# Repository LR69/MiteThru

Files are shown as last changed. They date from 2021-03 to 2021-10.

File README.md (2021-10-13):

# MiteThru

MiteThru is a raspberry based system used to count red mites going to/from a hen. 

It can count [one mite](https://www.youtube.com/watch?v=HM9iWV7Sr2Q),

VIDEO1 (https://www.youtube.com/watch?v=HM9iWV7Sr2Q)

Or, [many mites](https://www.youtube.com/watch?v=uRkvY6X4qfg) at the same time 

VIDEO2 (https://www.youtube.com/watch?v=uRkvY6X4qfg)

This MiteThru system uses :

- a raspberry pi 3 model B programmed using [python3](https://docs.python.org/3/) language,
- a native pi camera V2 Night Vision NoIR with a resolution of 8 mega-pixel,
- infrared Leds used to illuminate the mites,
- an electronic board with some push buttons, colored led and power devices to control the system,
- some Lego parts for a quick assembly.

The complete list of required components is available in the [Bill Of Materials](https://github.com/LR69/MiteThru/blob/master/Bill_Of_Material.ods)

# How the miteThru works:

A miteThru is a device that counts mites ascending and descending from a perch, where a hen is staying. It is able to classify them according to their size. The miteThru uses an infrared camera, to visualize the mites.

A circular boundary is placed around the roost. Mites passing inside this circle are considered "IN", mites outside are considered "OUT". To avoid indecision due to mites standing on the line, or moving around it, a counting or hysteresis zone is defined. The mite that is "OUT" has to cross the inner disc of the counting zone to go to "IN". The mite that is "IN" must cross the outer disc of the counting zone to go to "OUT".

## Counting principle

The miteThru places on the registered view :

- A monitoring area (in light gray) 
- A referencing zone (in dark gray)
- A counting area (in green)
- A border  (in red)

<table>
	<tr>
		<td width="300">  </td>
		<td>Step 1 : If a mite enters the tracking area, it is "seen" by the software, but has no visible identifier.</td>
	</tr>
	<tr>
		<td> </td>
		<td> Step 2 : If the mite fits into the referencing area, it is assigned an ID and its area is materialized by a colored disk that is superimposed on the image. The color of the disk indicates how the mite is classified according to its size. 

The size of the mite is updated with each image taken by the miteThru. </td>
	</tr>
	<tr>
		<td> </td>
		<td>Step 3: If the mite enters the counting area from the outside and leaves from the inside, the "IN" counter associated with its mite category is incremented.
If the mite enters the counting area from the inside and leaves from the outside, the "OUT" counter associated with its mite category is incremented.
		</td>
	</tr>
	<tr>
		<td></td>
		<td> Step 4: If the mite leaves the referencing area, it loses its identifier.
The identifiers are incremented as the mites enter the referencing area. 
The identifier can range from 0 to 99999. If a 100000th mite is tracked, its identifier returns to zero.</td>
	</tr>
	
</table>

# Commissioning

## Connecting the miteThru

The MiteThru uses a board equipped with LEDs and Push Buttons to start, stop and reset acquisitions locally. The board also power the IR LEDs illuminating the mites. All the schematics and Typon of the board can be found in the "[electronic board](https://github.com/LR69/MiteThru/tree/master/electronic%20board)" folder of this repository.

Connect the +5V power supply wires of the raspberry motherboard (brown and white wire), the +12V power supply of the circuit (wires coming from the AC/DC adapter), and the 2 wires of the infrared LEDs to the terminal block of the electronic board, as shown below. Make sure that the AC/DC adapter is not connected to the 230VAC wall socket during the connection operations.

Wiring the MiteThru

## Operating the MiteThru

3 push buttons are present on the [electronic board](https://github.com/LR69/MiteThru/tree/master/electronic%20board) :

MT_Buttons

## Start Acquisition 
Press the **<a name="start_BP">Start/Stop button</a>** for at least 3 seconds 
	→ The green LED flashes rapidly (several times per second), which means that the acquisition program is running.

<u>Note</u>: if the power supply is interrupted or if the power supply is disconnected while the program was running, it will restart automatically when the power is restored.

## Record Images

Press and hold the **<a name="record_BP"> Record button</a>**	
									→ Image recording starts
									→ Yellow LED lights up

Release of the **<a name="record_BP2"> Record button</a>**					
									→ Yellow LED goes out
									→ Image recording stops

## Stop Acquisition 

Press briefly the **<a name="start_BP2">Start/Stop button</a>** 
	→ The green LED goes out, which means that the acquisition program has stopped.

<u>Note</u>: After the program has been stopped, it can be restarted using the Start/Stop button, without losing the previous data. The new data are then added after the others.

## Reset Acquisition 

The miteThru must be turned off (green LED off) in order to begin the erasure procedure.

Press and hold the **<a name="reset_BP">Reset button</a>** 
	→ The green LED lights up blinks quickly.
	After about 5 seconds, the green LED lights up steadly 
	Release the **<a name="reset_BP">Reset button</a>** within 2 seconds
		→  The green LED lights up continuously for 2 seconds, then goes out. 

The miteThru is then cleared.

<u>Note</u>: After a RESET, the html pages of the miteThru do not automatically update, you must restart the acquisition program so that the "Data" and "Live" tabs update. In the same way, the "Images" tab will only be updated if new images are acquired.

# Monitoring and Data Recovery

The MiteThru embeds an Apache 2 server which provides a Web Interface, written in `html` and `php`. To access the interface, connect the MiteThru using Wifi or with an Ethernet cable. Then open a Browser and type the IP address of the MiteThru :

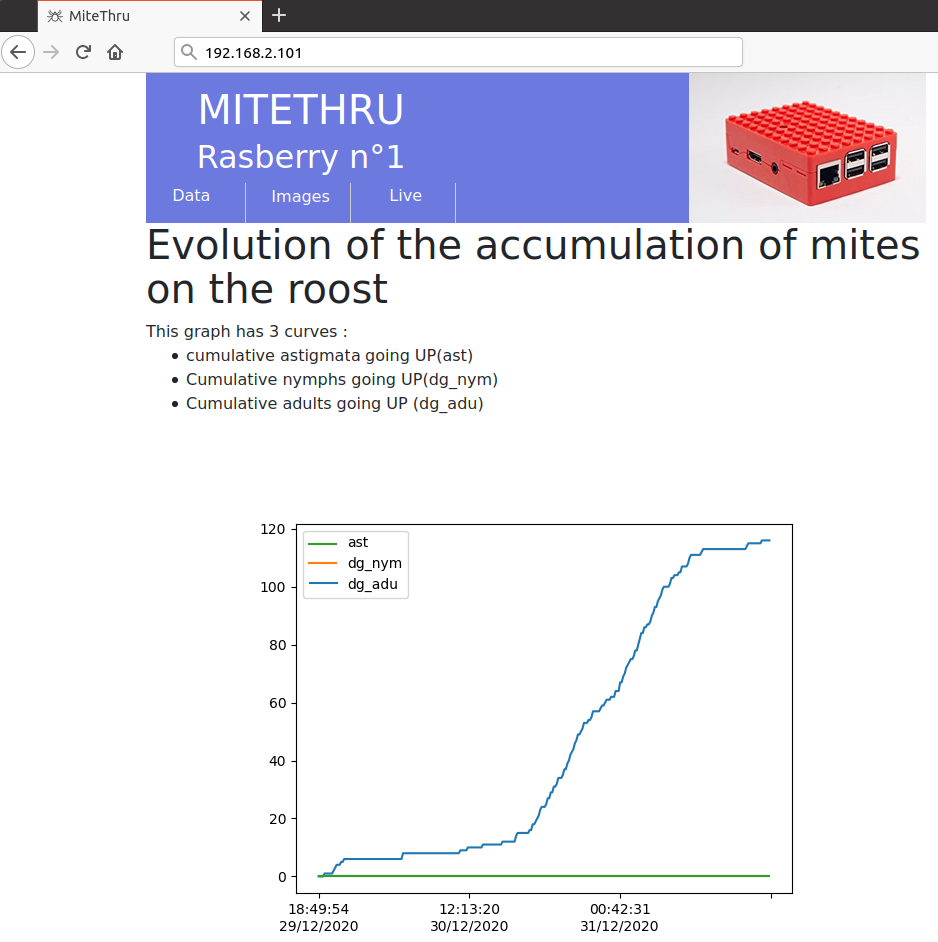
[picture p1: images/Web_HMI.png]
MT_HMI


## Tab "Data"

The web interface shows the temporal evolution of the Mites counted since the beginning of the acquisition. 3 diagrams can be seen :

- One showing the cumulative Mites going on the perch.
- An other showing  the cumulative Mites going down from the perch.
- A last one showing the instantaneous rate of climb or descent 

At the bottom of the tab, data of the experiment can be downloaded at `.csv` format by clicking on 
<div style="text-align:center">
	Button Download 
</div>

## Tab "images"

When the Push  [Record button](#record_BP)	 has been used to store images, this tab is used to check and download the images. Images are displayed as a link to the raw and processed images (at the bottom of the page). All the images of a record are available at download as a `.zip` file containing images at `.jpg` format. 

- Download the zip of the images by clicking on the links, then unzip the images and check that they are viewable. 
- If needed, jpeg images can be added (using [ffmpeg](https://www.ffmpeg.org/) for instance), to form a video like these presented at the top of this Readme. 

This tab can also be used to trigger automatically video acquisitions, on a certain level of mites being tracked at the same time, or on a periodic basis.

## Tab "Live"

On this page, two images are continuously updated by the program. 

1. The first image is the raw image take by the camera,
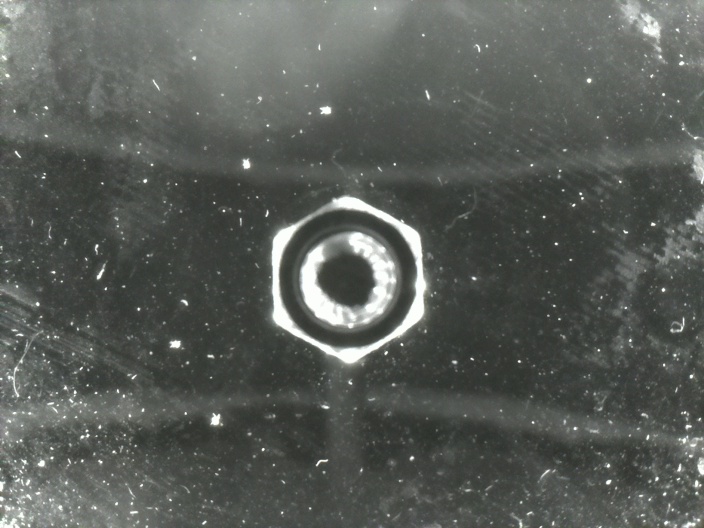
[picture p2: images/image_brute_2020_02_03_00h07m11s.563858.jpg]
image_brute
    
2. On the second image, elements related to image processing have been added.
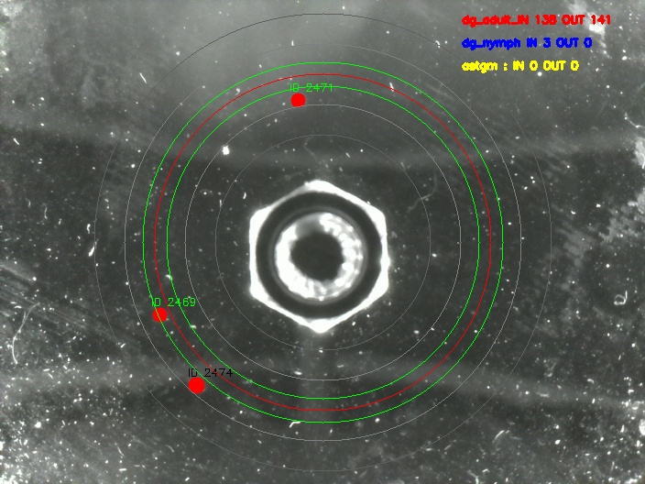
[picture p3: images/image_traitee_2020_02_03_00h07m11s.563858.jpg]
imag_traitée


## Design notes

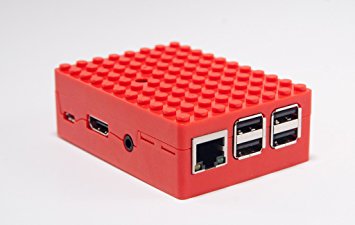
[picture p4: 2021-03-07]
raspberry/html/images/RPi_Lego.jpg

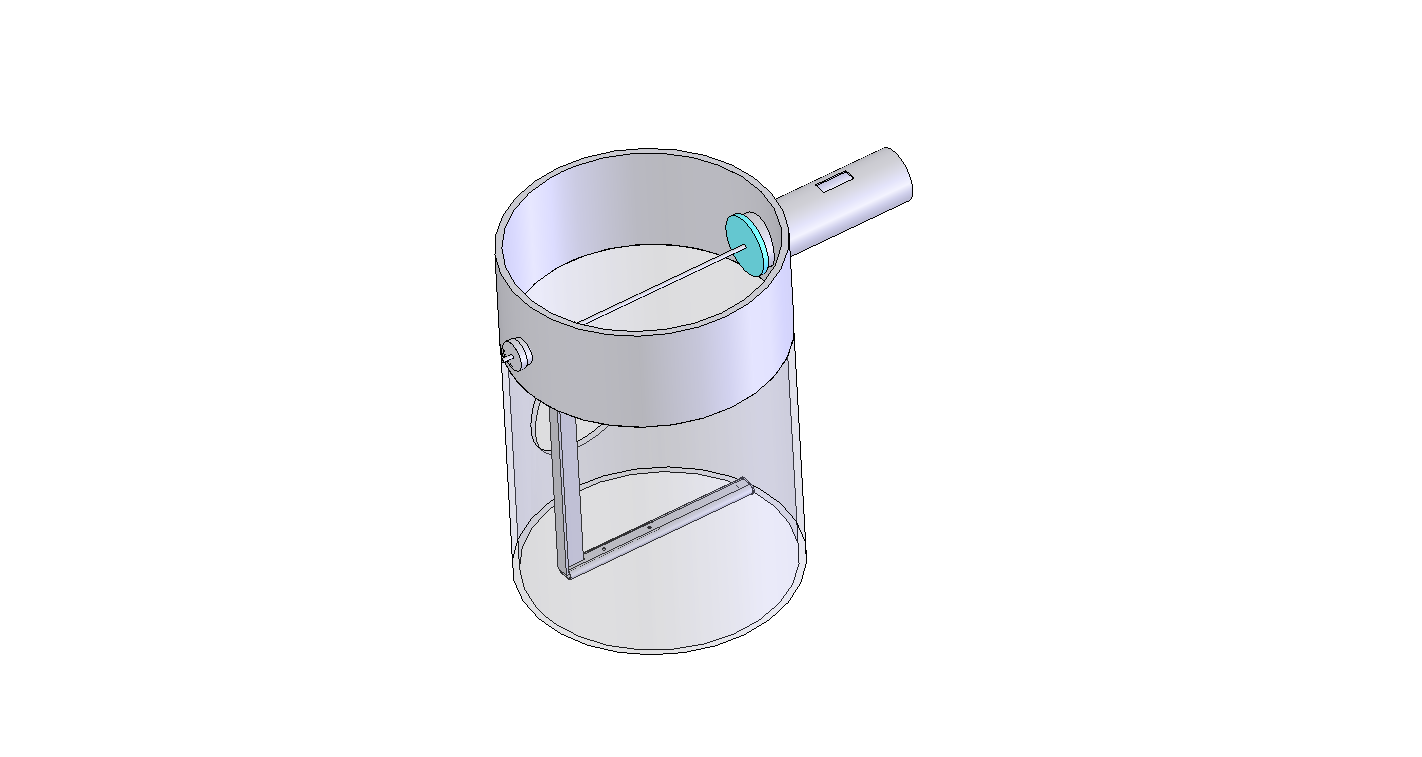
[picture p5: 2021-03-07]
technical drawings/mite_track_v1e.tif

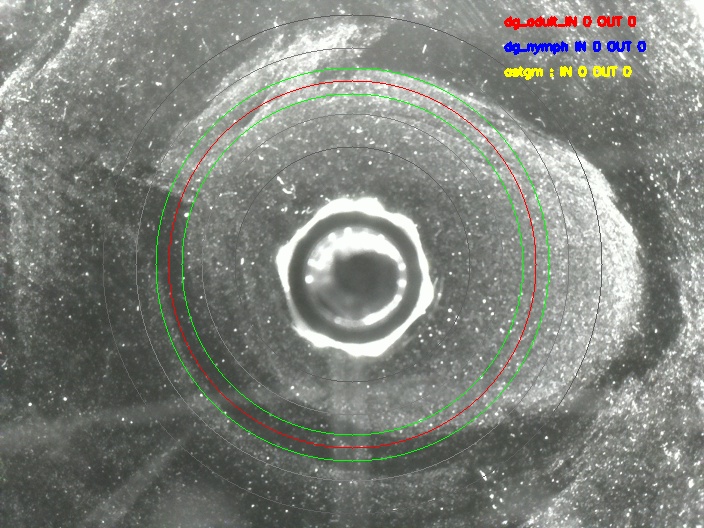
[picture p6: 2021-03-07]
raspberry/html/images_bugcount/live/image_traitee.jpg

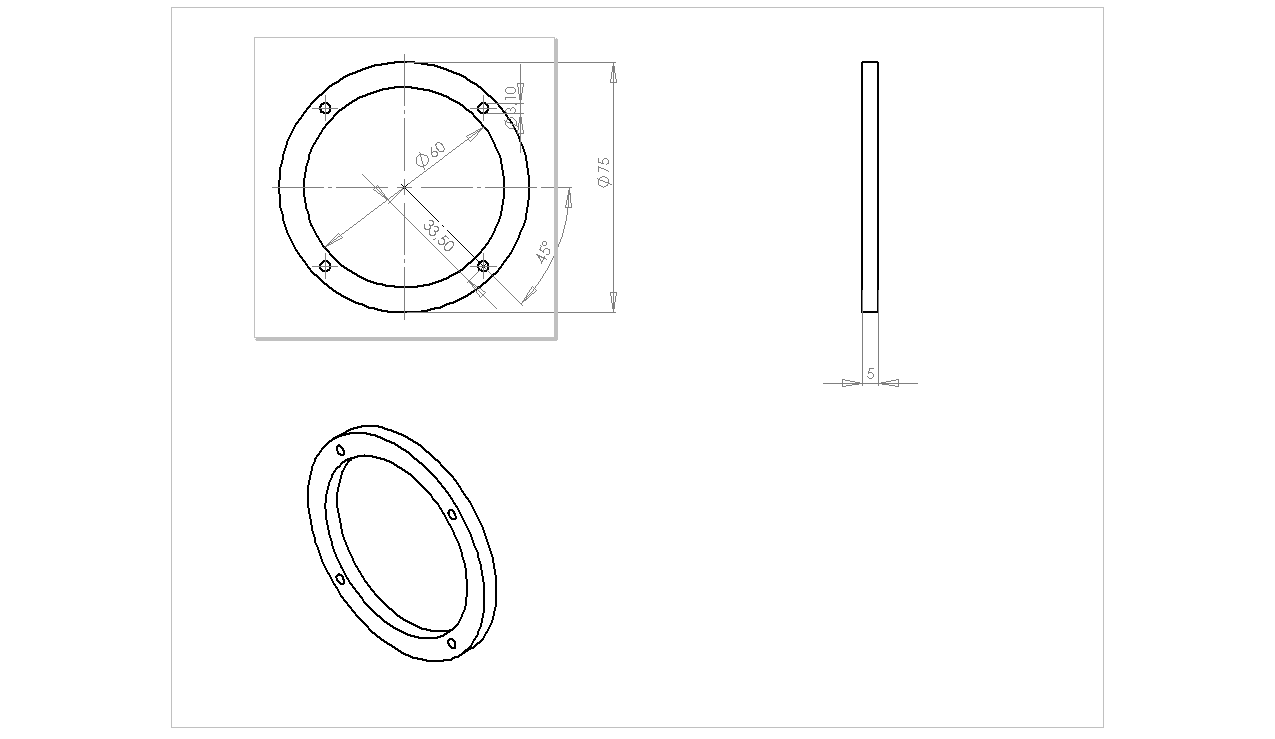
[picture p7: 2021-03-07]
technical drawings/washer.tif

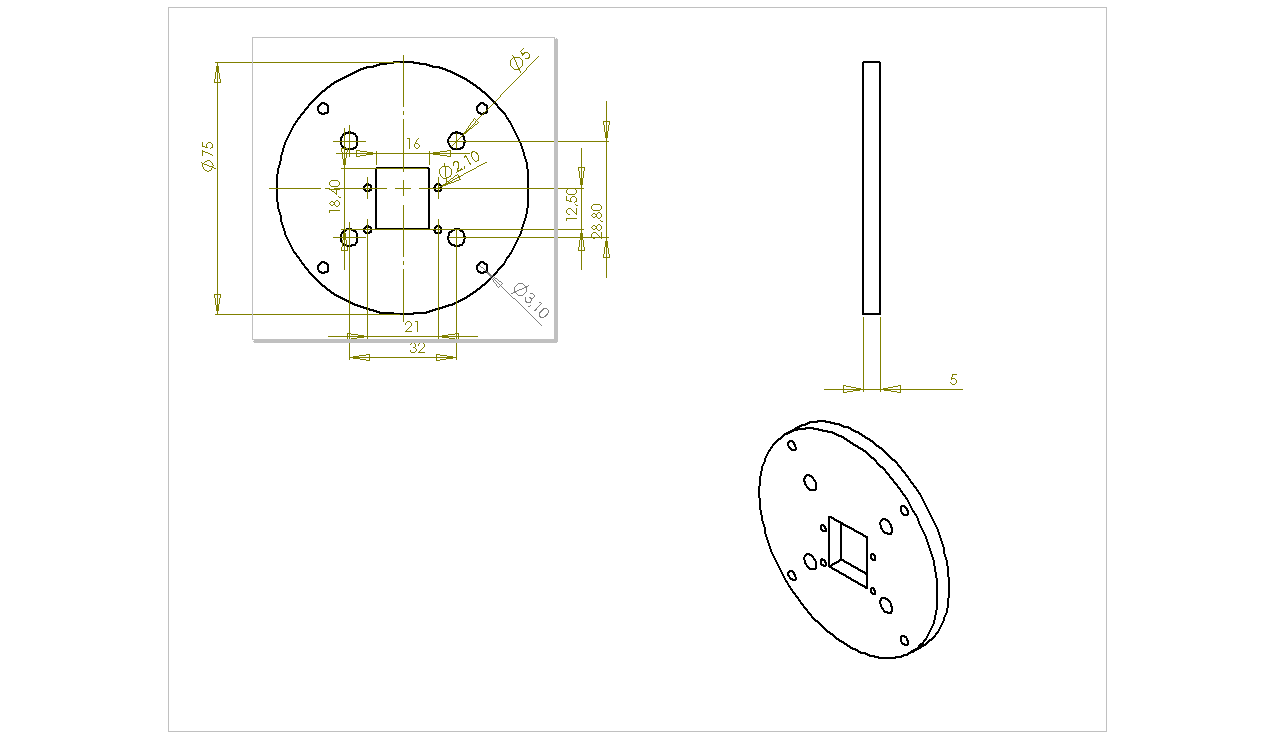
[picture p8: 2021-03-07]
technical drawings/camera_support.tif

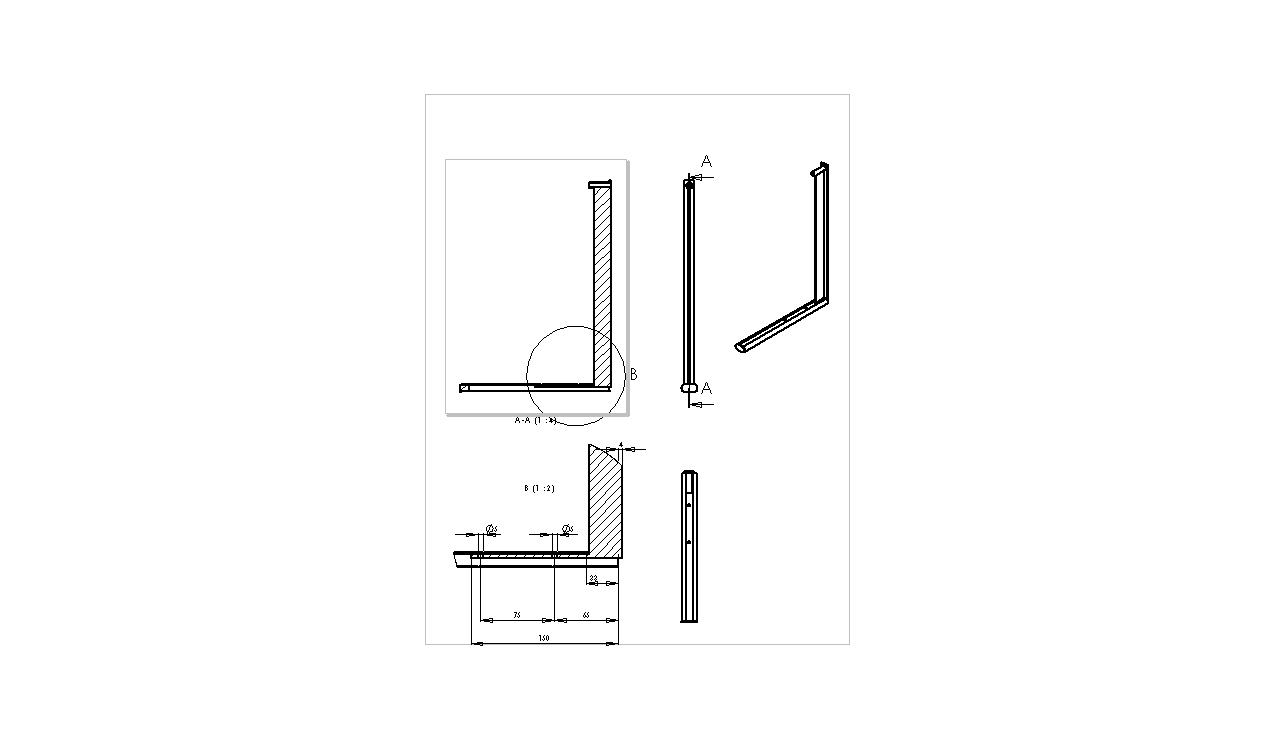
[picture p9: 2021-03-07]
technical drawings/balancoire_mbv1e.tif

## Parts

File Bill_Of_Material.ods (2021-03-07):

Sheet: MiteThru
Part | Description | Manufacturer | Reference | Quantity
Mechanics | Disc plexi diam :90mm thick : 5mm | Home made |  | 1
Mechanics | DiscPVC D75 mm for camera | Home made |  | 1
Mechanics | DiscPVC D75 mm for fan | Home made |  | 1
Mechanics | srew diam 4 mmround head L=25mm |  |  | 4
Mechanics | bolts diam 4 mm |  |  | 4
Mechanics | Screw diam 2 mm round head L=10mm |  |  | 4
Mechanics | Bolt diam 2 mm |  |  | 4
Mechanics | Tube PVC 80mm L=220mm |  |  | 1
Mechanics | threaded rod 3mm L= 120mm |  |  | 1
Mechanics | bolt 3mm |  |  | 2
Mechanics | lock washer 3 mm |  |  | 2
Mechanics | washer 3 mm |  |  | 2
Mechanics | Round 1 x 1 Straight Side | Lego | 4073 | 4
Mechanics | Brick 8x1 | Lego | 3008 | 1
Mechanics | Brick 6x1 |  | 3009 | 1
Mechanics | Brick 14x1 |  | 32018 | 2
Mechanics | Brick 8x1 w holes | Lego | 3702 | 3
Mechanics | Brick 6x1 w holes | Lego | 3894 | 1
Mechanics | Brick 1x1 |  | 3005 | 6
Mechanics | plate 6x2 |  | 3795 | 2
Mechanics | plate 4x1 |  | 3710 | 4
Mechanics | plate 8x1 |  | 3460 | 1
Mechanics | plate 8x2 |  | 3034 | 1
Mechanics | plate 14x2 |  | 91988 | 1
Computing | CBPIBLOX-YEL. - Pi Box, Raspberry Pi Model B, B+, 2 and 3 ABS | Multicomp |  | 1
Computing | Axial Fan, 40 x 40 x 10mm 11.4m3/h, 1,2W 12VDC
Computing | Raspberry 3 model B |  |  | 1
Computing | SD Card 16 GB UHS-I (U3) / Class 10 (C10) microSDHC/TF Flash Memory Card | Alertseal |  | 1
Computing | Raspberry Pi Module Caméra Raspberry Pi PiNoir Camera V2 |  |  | 1
Electronics | Strip 15 leds IR – L = 28cm IR 940nm | SOLAROX | IR1-60-940 | 1
Electronics | MOSFET, Canal-N, 47 A 55 V TO-220AB |  |  | 1
Electronics | AC/DC Adapter 12V c.c., 0 → 1A, 90 → 264V c.a., 12W |  |  | 1
Electronics | DC/DC Converter Vin 7 → 28V c.c., Vout 5V c.c., 500mA, 2.5W | RECOM |  | 1
Electronics | Pi RTC (DS1307) – only for server |  |  | 1
Electronics | polyester capacitor PET EPCOS, 1μF, ±10%, 40 V ac, 63 V dc, Through-hole, 5mm pitch, B32529 |  |  | 1
Electronics | D2,LED_JLED_THT:LED_D3.0mm |  |  | 1
Electronics | D1,LED_RLED_THT:LED_D3.0mm |  |  | 1
Electronics | D3,LED_VLED_THT:LED_D3.0mm |  |  | 1
Electronics | 2-contact PCB socket, through hole mounting, 5.08mm pitch, vertical |  |  | 2
Electronics | metallic film resistor 100Ω, 0,25W, |  |  | 1
Electronics | Resistor 270Ω, 0,25W, ±5% |  |  | 2
Electronics | resistor 680Ω, 0,25W, ±5% |  |  | 1
Electronics | resistor 10kΩ, 0,25W, ±5% |  |  | 1
Electronics | Tactile switch, 1NO - NO, 50mA/24Vdc, Black 5mm Push Button B3F-1020 | OMRON |  | 3

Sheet: Vocab
Statut
Commandé
Livraison en Cours
Reçu
Problème

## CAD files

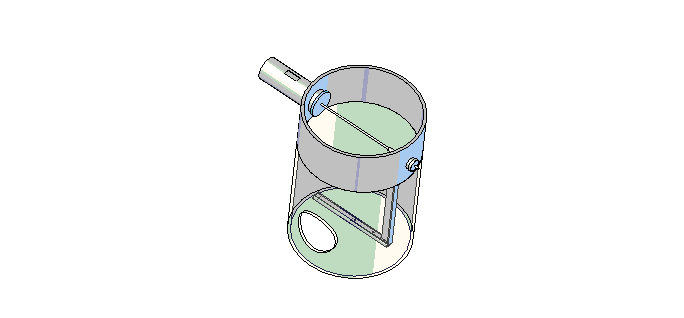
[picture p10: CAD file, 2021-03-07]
technical drawings/mite_track_v1e.SLDASM
Buse
tuyau
disque_plexi
tige filetée
TuyauDN40
bouchonDN40
Mesocosme
perchoir
montant
bouchon

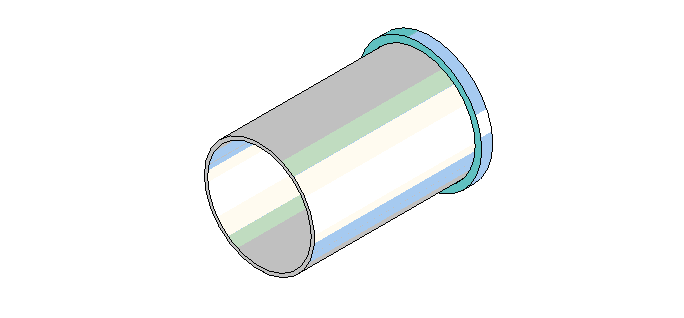
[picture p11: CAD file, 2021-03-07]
technical drawings/tuyau_disque_plexi.SLDASM
tuyau
disque_plexi

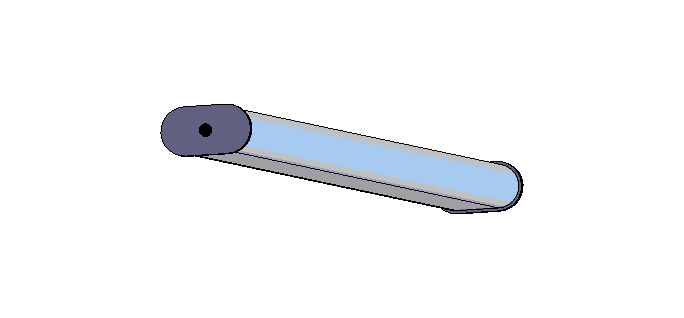
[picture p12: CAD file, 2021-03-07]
technical drawings/tige_bouchons.SLDASM
perchoir
bouchon x 2

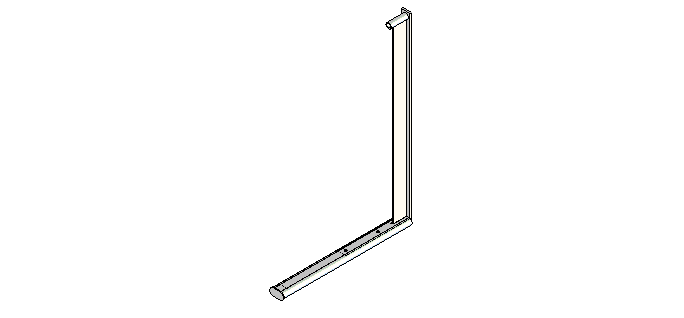
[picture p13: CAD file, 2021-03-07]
technical drawings/balancoire_mb.SLDASM
perchoir
montant
bouchon

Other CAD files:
technical drawings/Buse.SLDPRT
technical drawings/perchoir.SLDPRT
technical drawings/montant.SLDPRT
technical drawings/tige filetВe.SLDPRT
technical drawings/Mesocosme.SLDPRT
technical drawings/vis.SLDPRT
technical drawings/disque_plexi.SLDPRT
technical drawings/camera_support.SLDPRT
technical drawings/tuyau.SLDPRT
technical drawings/bouchonDN40.SLDPRT
technical drawings/TuyauDN40.SLDPRT
technical drawings/bouchon.SLDPRT
technical drawings/fan_support.SLDPRT
technical drawings/washer.SLDPRT
technical drawings/balancoire_mb.SLDDRW
technical drawings/camera_support.SLDDRW
technical drawings/fan_support.SLDDRW
technical drawings/montant.SLDDRW
technical drawings/tuyau.SLDDRW
technical drawings/washer.SLDDRW

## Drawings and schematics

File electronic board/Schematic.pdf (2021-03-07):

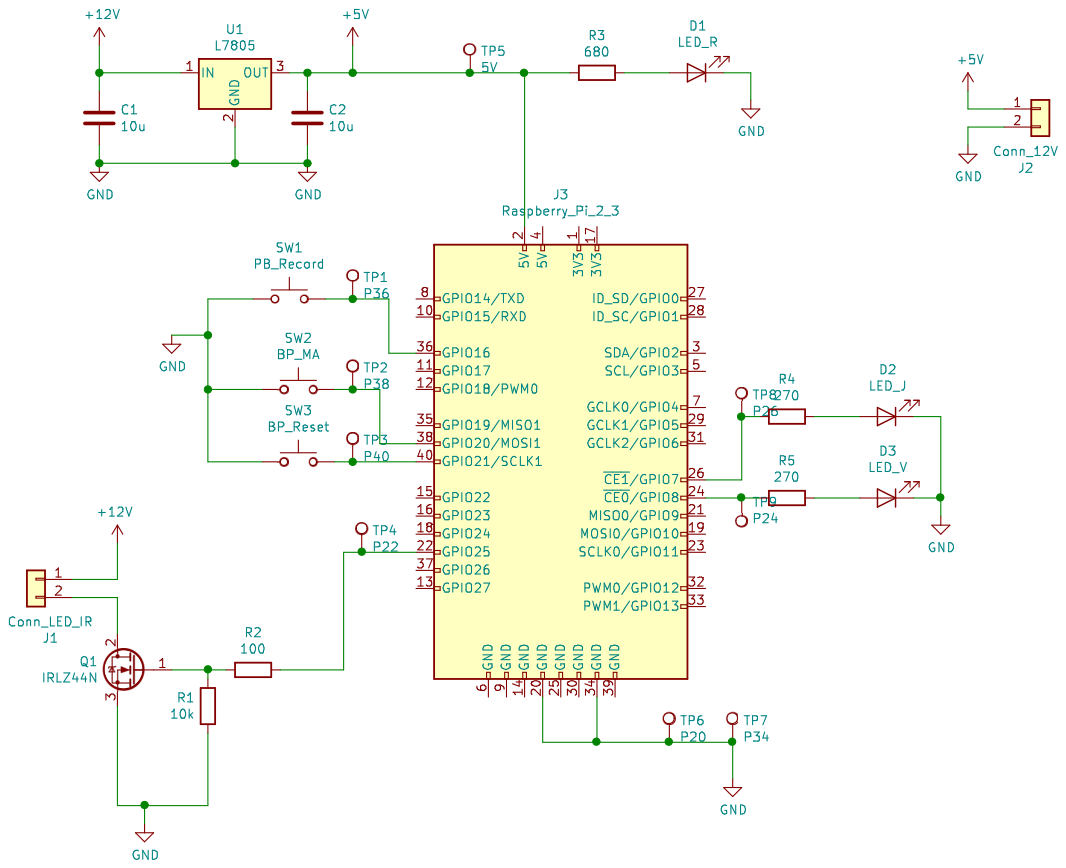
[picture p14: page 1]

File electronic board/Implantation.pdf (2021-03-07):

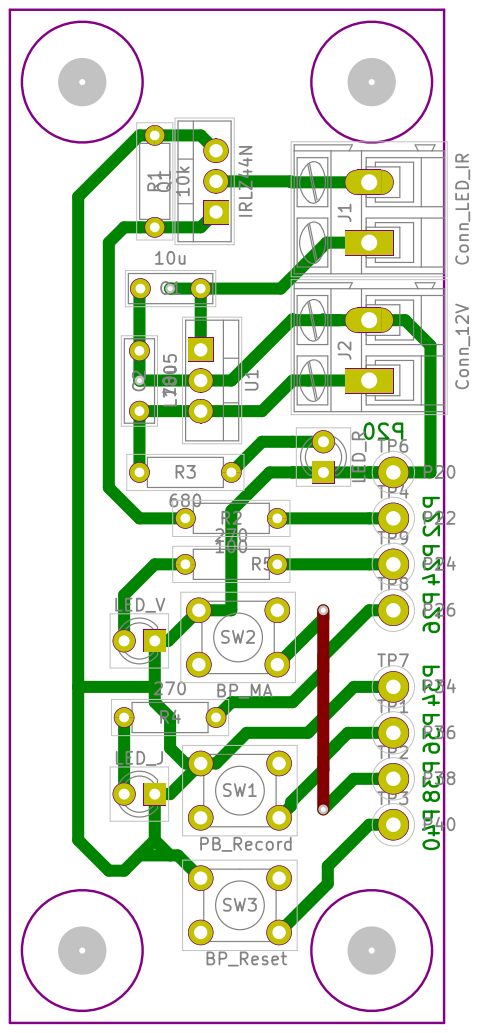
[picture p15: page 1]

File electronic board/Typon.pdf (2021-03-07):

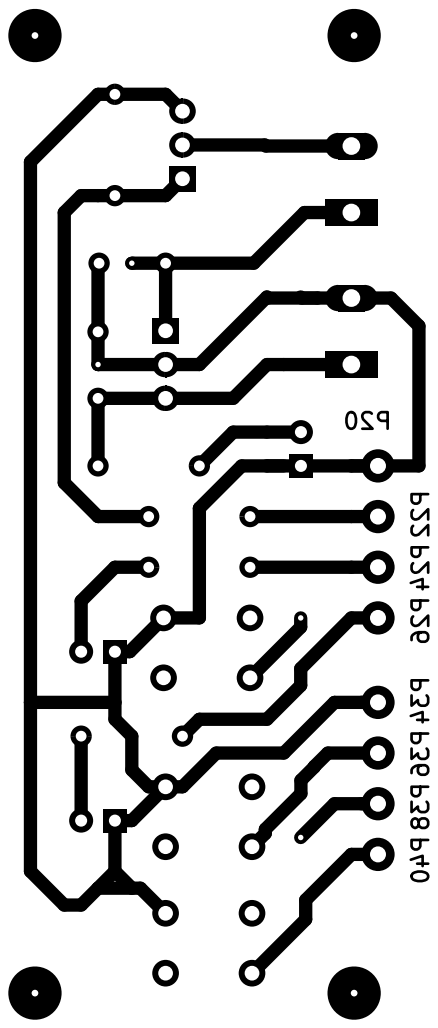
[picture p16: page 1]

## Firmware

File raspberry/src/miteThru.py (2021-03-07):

from picamera.array import PiRGBArray
from picamera import PiCamera
import numpy as np
import math
from random import randint
import cv2
import RPi.GPIO as GPIO
import time
import os
import shutil
import datetime
import sys
import bugcount_utils
import img_count_utils as imcount
from mitestracker import MitesTracker
import copy
import multiprocessing as mp #MP
import signal #MP

"""
# MiteThru version 12 du 16 juillet 2020
 """

os.nice(-5) # le programme principal est agressif

#initialisation de l'interface images
shutil.copyfile("/var/www/html/pre_index_images_ini.html", "/var/www/html/pre_index_images.html")

#Vérification de la conformité de la commande passée :
msg_gal = "ERREUR : rappel de la commande miteThru : python3 miteThruVi.py -Fe f -mode mode [s] [d] [i]"
if len(sys.argv) < 5:
	print(msg_gal)
	print("Le nombre d'argument doit être >= 3")
	sys.exit(1)

mode = sys.argv[4]
option = ""
if mode == "debug" or mode == "normal":
	if len(sys.argv) != 6:
		print(msg_gal)
		print("mode \"{}\", il faut un seul argument après le mode".format(mode))
		sys.exit(1)
	try:
		s=int(sys.argv[5])
	except ValueError:
		print(msg_gal)
		print("L'argument après le mode doit être un nombre entier")
		sys.exit(1)
elif mode == "calib_en_ligne":
	option = "calib_en_ligne"
	mode = "video"
	p0_flag = False
elif mode == "video" :
	if len(sys.argv) != 8:
		print(msg_gal)
		print("mode \"{}\", il faut 3 arguments après le mode".format(mode))
		sys.exit(1)
	try:
		s=int(sys.argv[5])
		s=int(sys.argv[6])
		s=int(sys.argv[7]) 
	except ValueError:
		print(msg_gal)
		print("L'argument après le mode doit être un nombre entier")
		sys.exit(1)
else:
	if mode != "calib":
		print(msg_gal)
		print("Le mode \"{}\" n'est pas reconnu".format(mode))
		sys.exit(1)

# gestion des modes 
seuil_video = 9999
duree_video = 1
intervalle_min_video = 99999
debug = 0
if (mode == "video"):
	seuil_video = int(sys.argv[5]) # nombre d'acariens suivis déclenchant une acquisition video
	duree_video = int(sys.argv[6]) # duree de l'acquisition vidéo (en secondes)
	intervalle_min_video = int(sys.argv[7]) # intervalle minimum entre deux acquisitions videos (en secondes)
	texte="<h1>Aquisition automatique de vidéos</h1>\n <ul>\n"
	if option != "":
		texte+="<li>option : {}</li>\n".format(option)
	texte+="<li>nombre d'acariens suivis déclenchant une acquisition video : {}</li>\n".format(seuil_video)
	texte+="<li>duree de l'acquisition vidéo (en secondes) : {}</li>\n".format(duree_video)
	texte+="<li>intervalle minimum entre deux acquisitions videos (en secondes):{}</li>\n</ul>\n".format(intervalle_min_video)

elif (mode == "normal"):
	texte="<h1>Aquisition automatique de vidéos</h1>\n \n"
	if int(sys.argv[5]) == 0:
		texte+="<p> L'acquisition automatique a été désactivée par l'utilisateur.</p>"
	else:
		texte+="<p> L'acquisition automatique a été désactivée car la taille totale des images sur la carte SD dépasse 1GB. Pensez à faire un Reset.</p>"
elif (mode == "calib"):
	texte="<h1>Aquisition automatique de vidéos</h1>\n \n"
	texte+="<p> Le miteThru est en mode CALIBRATION. L'acquisition est forcée à une image par seconde.</p>"
	texte+="<p> Aucun enregistrement vidéo n'est effecué.</p>"
	texte+="<p> Les données d'aires sont mémorisée dans un fichier \"data.csv\".</p>"
elif (mode == "debug"):
	debug = int(sys.argv[5]) # niveau de nervosité du debug 
	texte="<h1>Aquisition automatique de vidéos</h1>\n \n"
	texte+="<p> Le miteThru est en mode Debug. avec un niveau de verbosité de {}</p>".format(debug)
# Gestion de la fréquence d'échantillonnage
try:
	Fe = int(sys.argv[2]) # fréquence d'échantillonage
except ValueError:
	print(msg_gal)
	print("La frequence d'échantillonnage doit être un nombre entier")
	sys.exit(1)

with open('/var/www/html/pre_index_images.html','a') as preamb:
	if Fe == 0 :
		texte+="<p> La fréquence d'échantillonnage n'est pas limitée</p>"
	else:
		texte+="<p> La fréquence d'échantillonnage maximale est fixée à {} images par secondes</p>".format(Fe)
	texte+="<p></p>"
	texte+="<h1>Images mémorisées </h1>\n"
	texte+="\t<div align=center>\n"
	texte+="\t\t<table>\n"
	preamb.write(texte)
	print(texte) #pour le log
if Fe == 0:
	Fe = 99999 # pas de limitation
temps_cycle = 1000/Fe #temps de cycle minimum


# pour le mode debug 8 = forçage de reset 
bypass_reset = False
if debug == 8:
	bypass_reset = True
	with open("stop_normal",'w') as mon_fichier:
		mon_fichier.write("forçage de reset en mode debug")
		

# gestion du redémarrage après coupure de courant
if os.path.exists("stop_normal"):
	bypass = False
else:
	bypass = True

# pour le mode debug 9 = forçage de lancement
if debug == 9:
	bypass = True

# initialisation des pins du rpi
GPIO.setmode(GPIO.BCM)
GPIO.setwarnings(False)

# entrées
BPrecord = 16 # Bouton enregistrement : pin 36
GPIO.setup(BPrecord, GPIO.IN,pull_up_down=GPIO.PUD_UP) 
BPma = 20  # bouton marche arrêt : pin 38
GPIO.setup(BPma, GPIO.IN,pull_up_down=GPIO.PUD_UP)  
BPreset = 21 # bouton de reset : pin 40
GPIO.setup(BPreset, GPIO.IN,pull_up_down=GPIO.PUD_UP)  

# sorties
PWR_LED = 25 # pin 22 
GPIO.setup(PWR_LED, GPIO.OUT) # commande des leds de puissance (via transistor)
LED_V = 8 # pin 24
GPIO.setup(LED_V, GPIO.OUT) # commande de led verte fonctionnement normal et effacement
LED_J = 7 # pin 26
GPIO.setup(LED_J, GPIO.OUT) # commande de led jaune enregistrement

#https://docs.opencv.org/3.3.0/d3/db4/tutorial_py_watershed.html
# initialize the camera and grab a reference to the raw camera capture
camera = PiCamera()
camera.resolution = (704, 528) #(704, 528), (1024,768) ou (3200, 2404)
camera.framerate = 24
camera.brightness = 70
camera.contrast = 50
rawCapture = PiRGBArray(camera, size=(704, 528)) # à changer aussi !
time.sleep(2)
(w, h) = camera.resolution




# dimension du cercle frontière (version commune)
center = (int(w / 2), int(h / 2))
rayon = int(0.35*h)
trackW = int(0.25*h) # largeur de la zone de traçage
countW = int(0.05*h)  # largeur de la zone de comptage
if (debug >=1 or mode == "calib"):
	print("largeur de la zone de suivi : {}".format(trackW))
	print("largeur de la zone de comptage : {}".format(countW))

#initialisation mite tracker

mt = MitesTracker((w, h), (center, rayon), trackW, countW, 50)
mt_old = copy.copy(mt)
IMGcount = 0
BPcount = 0
instants_acquisition=[]
taux_franchissement_montee=[]
taux_franchissement_descente=[]
instants_cumuls=[]
cumul_ast_montee=[]
cumul_dg_nym_montee=[]
cumul_dg_adu_montee=[]
cumul_ast_descente=[]
cumul_dg_nym_descente=[]
cumul_dg_adu_descente=[]
jobs=[] #MP
dt_frame_ms = 0 # temps d'acquisition et de traitement d'une image
dt_frame_min = 500 # valeur mini de dt_frame_ms observée
dt_frame_max = 0 # valeur maxi de dt_frame_ms observée
while(True): 
	maintenant = datetime.datetime.now()
	date = maintenant.strftime('%Y-%m-%d')
	heure = maintenant.strftime('%H:%M:%S')
	if (GPIO.input(BPreset) == 0)and (GPIO.input(BPma) == 1): # on APPUIE sur le BP de reset
		BPcount += 1
		GPIO.output(LED_V,True)
		print("appui sur BPreset n=",BPcount)
		if ((BPcount > 20) and (BPcount<40)): # on est resté appuyé pendant 2s
			if (BPcount%2) == 0 :
				GPIO.output(LED_V,True) 
			else:
				GPIO.output(LED_V,False)
		if (BPcount >= 40): # on est resté appuyé trop longtemps
			GPIO.output(LED_V,False)
	if (GPIO.input(BPreset) == 1) and (GPIO.input(BPma) == 1): # on N'APPUIE PAS sur le BP de reset
		if ((BPcount > 20) and (BPcount<40) or bypass_reset): # on a relâché pendant le clignotement
			# initialisation des fichiers : A RENDRE CONDITIONNEL PAR APPUI GPIO
			print("{} {} : EFFACEMENT DONNEES".format(date,heure))
			GPIO.output(LED_V,True)
			bugcount_utils.reinit(option)
			IMGcount = 0
			bypass_reset = False
			time.sleep(1)
		BPcount =0 
		# Extinction LEDs
		GPIO.output(LED_V,False)
		GPIO.output(PWR_LED,False) 

	if ((GPIO.input(BPma) == 0) and (GPIO.input(BPreset) == 1) or bypass): # on APPUIE sur le BP de marche et pas sur Reset
		print("appui sur BPmarche n=",BPcount)
		BPcount += 1
		if ((BPcount>10) or bypass): #on lance le démarrage du programme
			fichier_flag = "stop_normal"
			if os.path.exists(fichier_flag):
				os.remove(fichier_flag)
			print("{} {} : On lance le programme principal de vision".format(date,heure))
			GPIO.output(PWR_LED,True) # On allume les LEDS de puissance
			derniere_donnee = datetime.datetime.now() # pour respecter le temps entre 2 données dans le tableau
			REC = False
			debut_video = derniere_donnee
			stop_video = derniere_donnee
			while (GPIO.input(BPma) == 0):
				time.sleep(0.1)# on attend le relâchement du bouton
			num_img = 0
			t_init = datetime.datetime.now()
			
			#dossier_images_test = "/root/Bugcount/images_test3" #pour test sans caméra
			#liste_images = os.listdir(dossier_images_test ) #pour test sans caméra
			#liste_images.sort() #pour test sans caméra
			#for f in liste_images: #pour test sans caméra
				#print("image:{}".format(f)) #pour test sans caméra
				#chem = dossier_images_test + "/" + f #pour test sans caméra
				#capt = cv2.imread(chem)  #pour test sans caméra
			
			for frame in camera.capture_continuous(rawCapture, format="bgr", use_video_port=True):# à remettre avec caméra
				#acquisition image
				capt = frame.array # à remettre avec caméra				
				GPIO.output(LED_V,True)
				img=capt.copy() 
				GPIO.output(LED_V,False) # on a pris une image
				# creation du masque
				mask = np.zeros((h,w),np.uint8)
				cv2.circle(mask,center,int(rayon),(255,255,255),trackW)

				# traitement 
				cercles, fourmi = imcount.bugcount(img, mask, mt.AREA_MIN_ACA, mt.AREA_MAX_ACA, mode)
				#print(cercles)
				if num_img < 20 :
					cercles=[]
					num_img += 1
				objects = mt.update(cercles) 
				delta_acariens = mt - mt_old
				# loop over the tracked objects
				l_objectID=[]
				l_nature=[]
				l_etat=[]
				l_area=[]
				for (objectID, centroid) in objects.items():
					# draw both the ID of the object and the centroid of the
					# object on the output frame
					if (mt.etat[objectID] == 'IN') :
						couleur_ID = (0, 255, 0)
					else:
						couleur_ID = (0, 0, 0)
					text = "ID {}".format(objectID)
					cv2.putText(img, text, (centroid[0] - 10, centroid[1] - 10),
						cv2.FONT_HERSHEY_SIMPLEX, 0.4, couleur_ID, 1)
					if mt.nature[objectID] == 'ASTIGMATA' :
						couleur_cercle = mt.couleur_ASTIGMATA 
					elif mt.nature[objectID] == 'DG_NYMPH' :
						couleur_cercle = mt.couleur_DG_NYMPH
					elif mt.nature[objectID] == 'DG_ADULT' :
						couleur_cercle = mt.couleur_DG_ADULT 
					else: 
						couleur_cercle = (255,0,255)
					cv2.circle(img, (centroid[0], centroid[1]), int(math.sqrt(mt.areas[objectID]/math.pi)), couleur_cercle, -1)
					# ajout du mode "étalonnage en ligne"
					if mt.franchissement[objectID] and option == "calib_en_ligne":
						l_objectID.append(objectID)
						l_nature.append(mt.nature[objectID])
						l_etat.append(mt.etat[objectID])
						l_area.append(mt.areas[objectID])
				if len(l_objectID) >0:
					#print("écriture :  {}".format(l_objectID))
					if not p0_flag:
						p0 = mp.Process(target=bugcount_utils.ecrire_aire_en_ligne, args = (l_objectID, date,heure,l_nature,l_etat,l_area))  #MP
						p0.start()  #MP
						p0_flag = True
					elif not p0.is_alive():
						p0 = mp.Process(target=bugcount_utils.ecrire_aire_en_ligne, args = (l_objectID, date,heure,l_nature,l_etat,l_area))  #MP
						p0.start()  #MP
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

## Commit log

2021-03-07 initial publication - miteThru version 12
    [IDs.csv, aires.csv, data.csv, etats.csv]
2021-03-07 electronics and mechanical design
    [Bill_Of_Material.ods, Buse.SLDPRT, Mesocosme.SLDPRT, TuyauDN40.SLDPRT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]
